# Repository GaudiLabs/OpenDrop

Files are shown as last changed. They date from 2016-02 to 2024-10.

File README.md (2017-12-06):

## OpenDrop 

Open Source Digital Microfluidics Bio Lab

### Don't click on the files!
Click on the "Download ZIP" Button to the right.
Then unpack the archive.

### Open Source Digital Microfluidics Bio Lab

OpenDrop is a new design for an open source digital microfludics platform for research purposes. The device uses recent electro-wetting technology to control small droplets of liquids. Potential applications are lab on a chip devices for automating processes of digital biology. How ever the present design should also open the technology to other field and allow experimentation to find new applications. Including the field of art, music, games and education.

For more info on the open source project see:

http://www.gaudi.ch/OpenDrop

### License

OpenDrop, all design files and software are licensed under a GNU GENERAL PUBLIC LICENSE
See license file in the repository.

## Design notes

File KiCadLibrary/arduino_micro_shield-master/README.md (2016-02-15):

arduino_micro_shield
====================

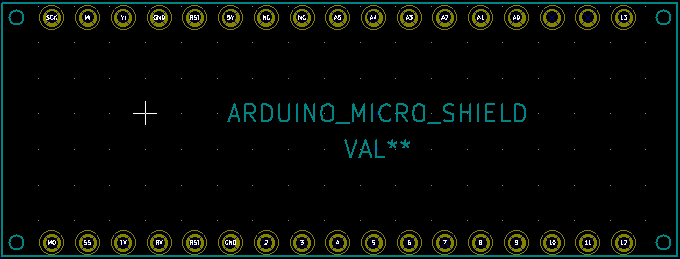
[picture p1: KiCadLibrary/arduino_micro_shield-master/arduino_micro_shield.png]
My image


KiCAD library and footprint for an Arduino Micro shield.

This is a component which represent the Arduino Micro pinout,
and a footprint for that component which maps to the surface area
and pinout of the Micro.

Pull requests very welcome!

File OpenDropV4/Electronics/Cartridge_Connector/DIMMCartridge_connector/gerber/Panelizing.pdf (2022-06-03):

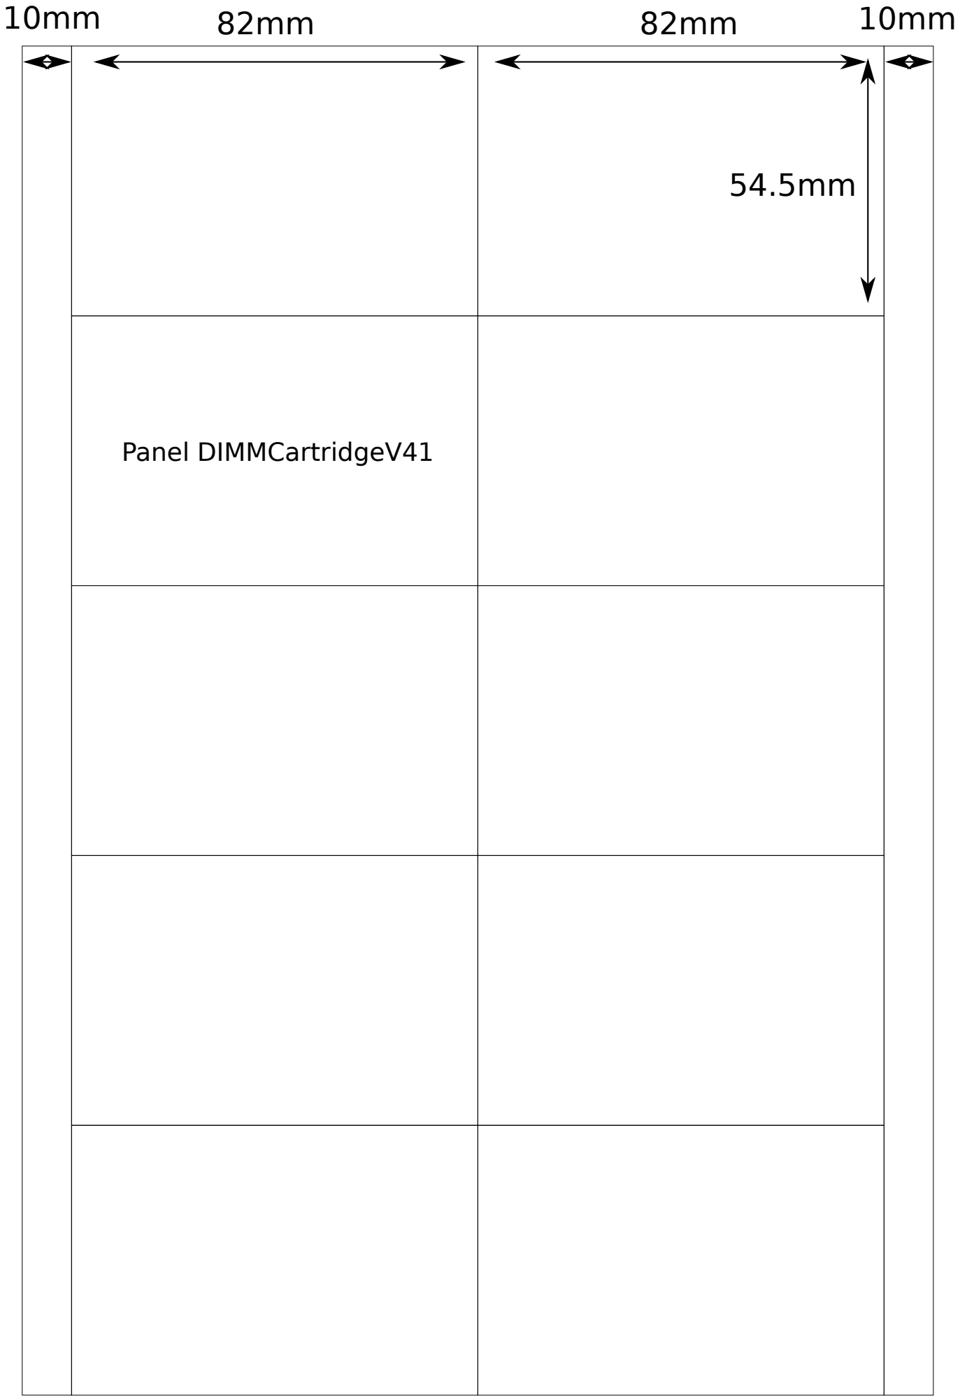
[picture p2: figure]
Panel DIMMCartridgeV41

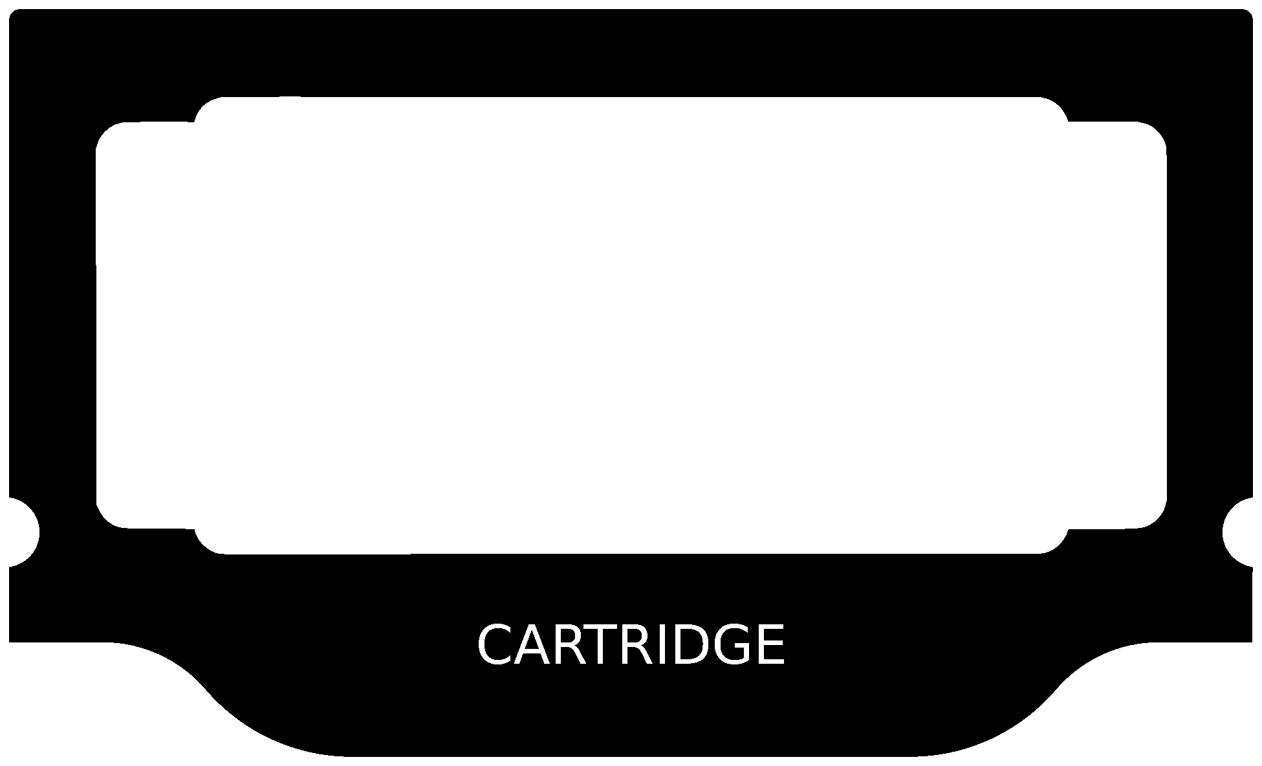
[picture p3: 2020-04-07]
OpenDropV4/Electronics/OpenFrame/design/DimmTopSilk.png

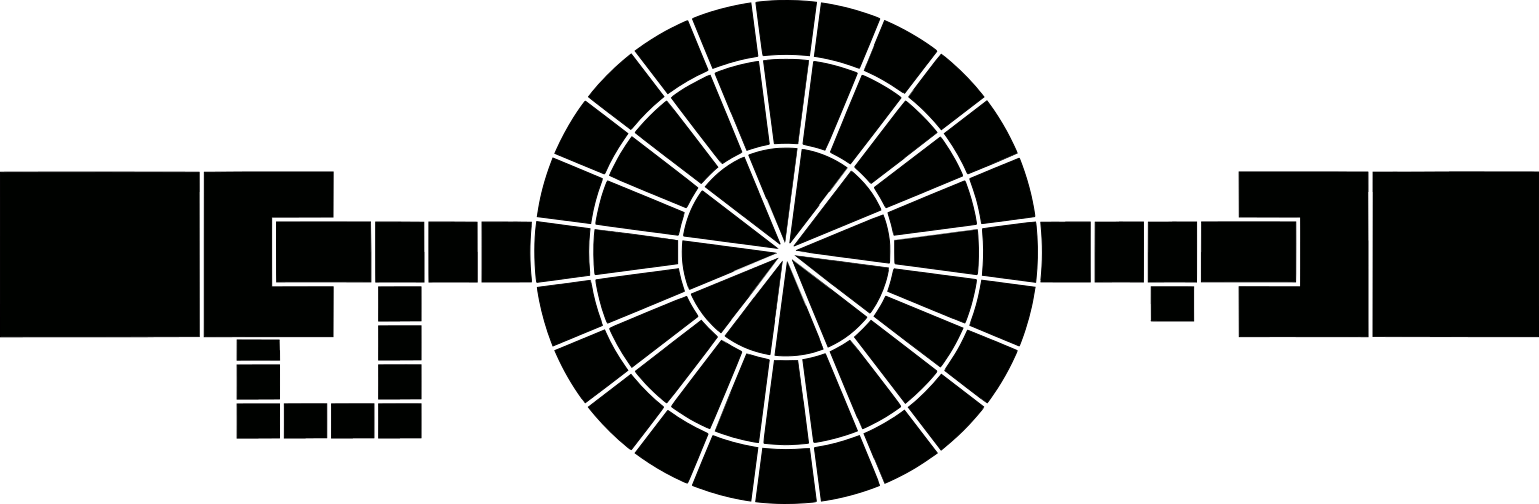
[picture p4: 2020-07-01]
OpenDropV4/Electronics/CartridgeV4/DIMMCartridgeV4/svg/path104085-4.png

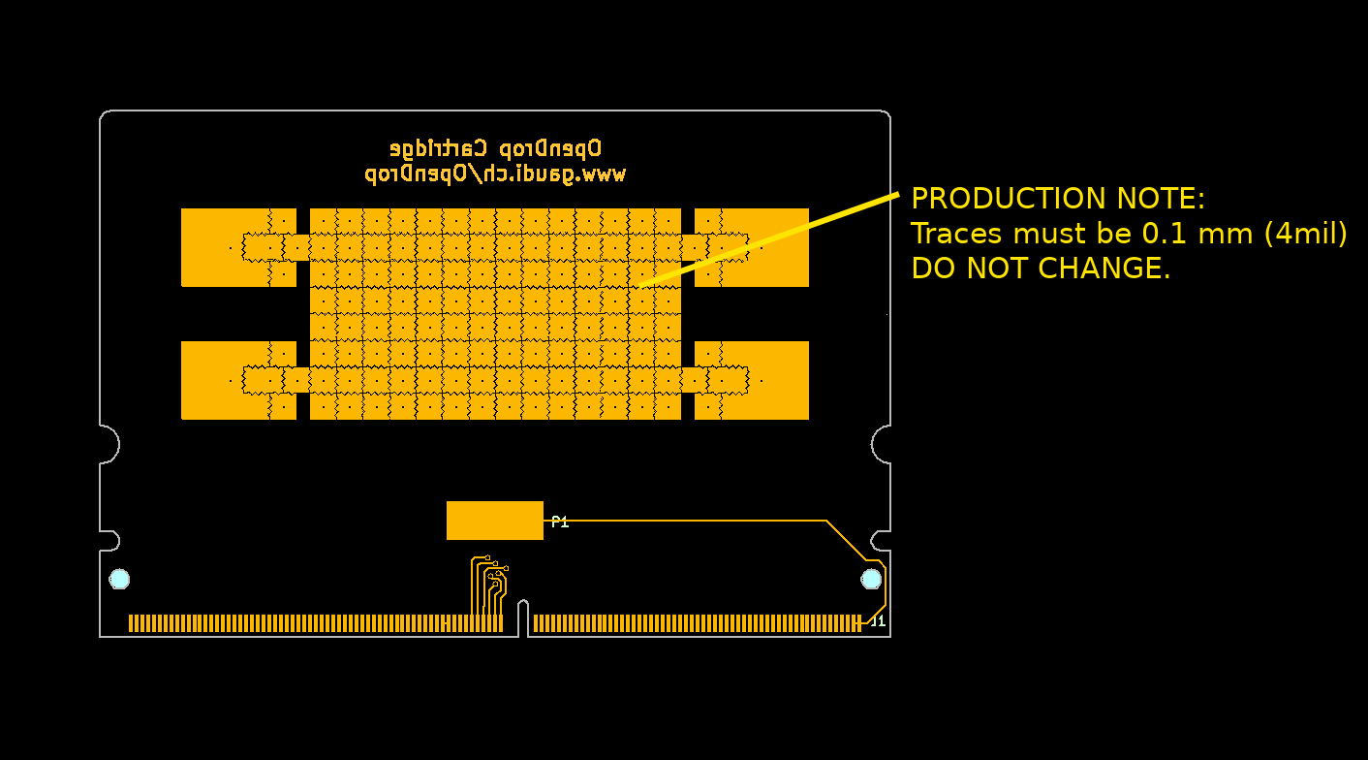
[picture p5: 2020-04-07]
OpenDropV4/Electronics/CartridgeV4/DIMMCartridgeV4/gerber/ProductionNote.png

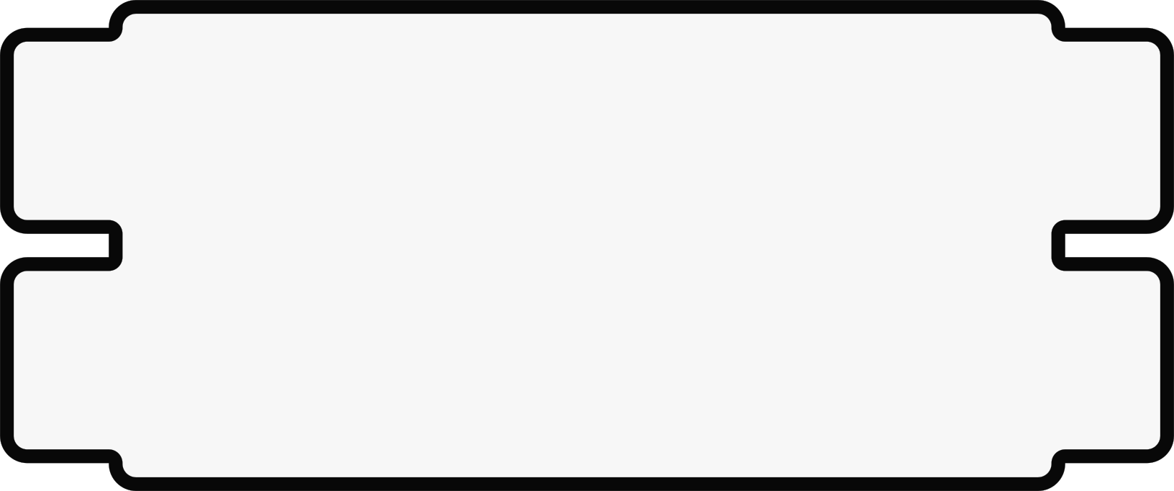
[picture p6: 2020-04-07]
OpenDropV4/Electronics/CartridgeV4/DIMMTop/design/DimmTopCooper.png

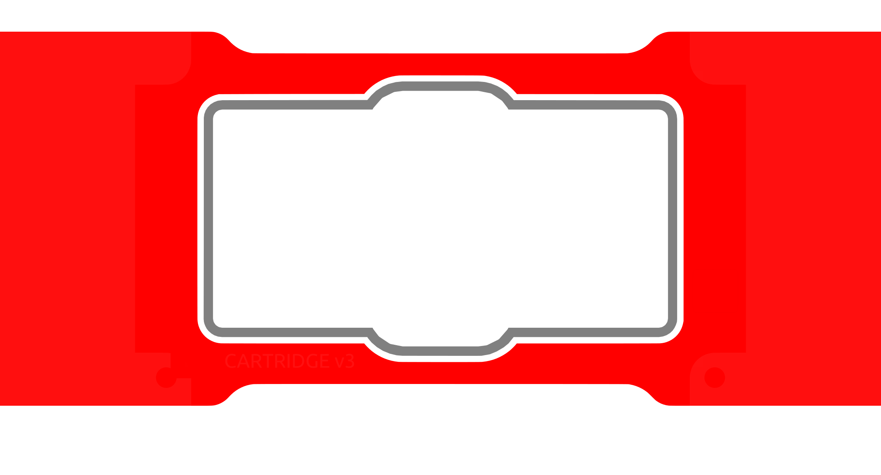
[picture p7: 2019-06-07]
OpenDropController4_25/OpenDropFrame.png

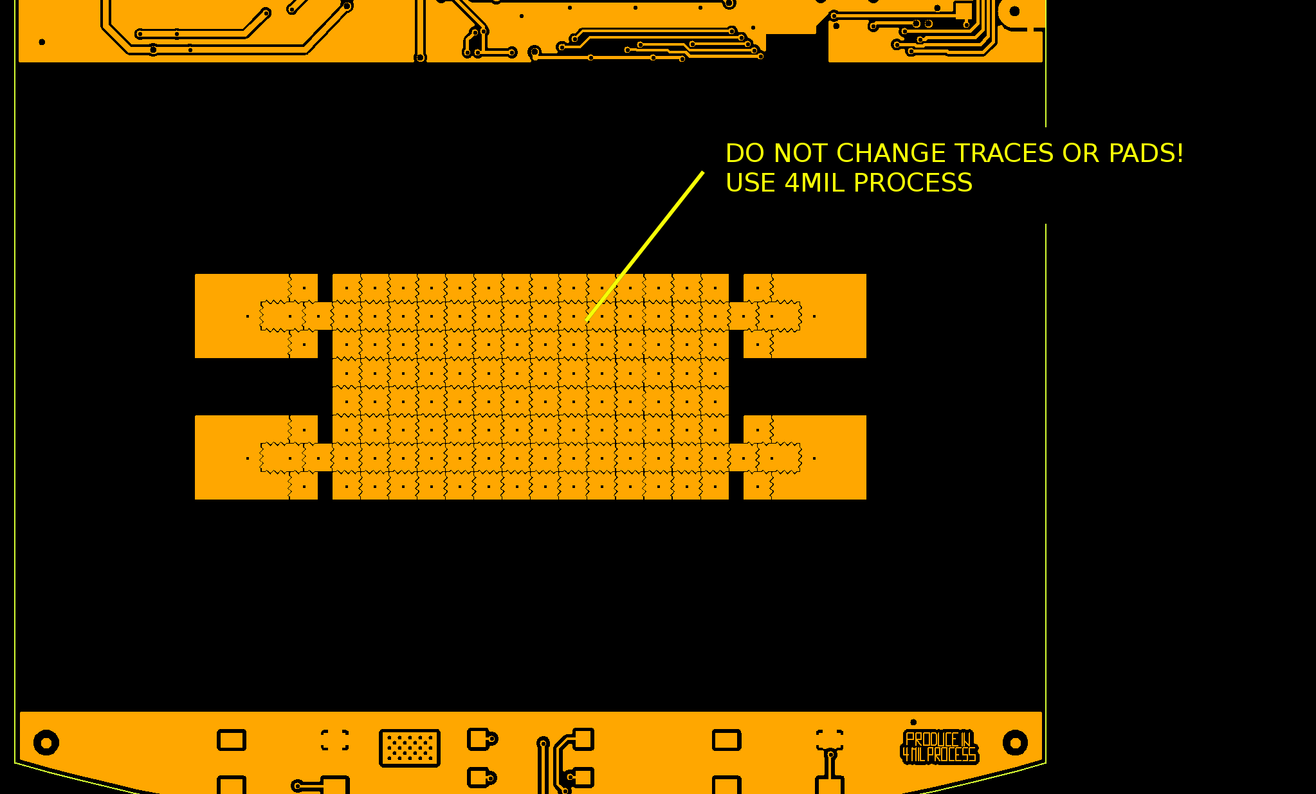
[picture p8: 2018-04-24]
OpenDropV4/PCB/OpenDropV4/Gerber/ProductionNote_OpenDropV3.png

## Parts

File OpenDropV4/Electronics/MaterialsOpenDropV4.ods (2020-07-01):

 | Materials OpenDrop V4 |  | 19. Mai 2020
 | Quantity | Designation | Order No | Manufacturer
Main Board
 | 1 | Switch_On-On | SS 25136 NH, 642-ADTSM62RVTR 642-25136NLDH | Reichelt Mouser
 | 4 | Spacer | DI 15MM | reichelt
 | 4 | Screws M3x 8mm | BN1435.03008 | Hasler.ch /bossard
 | 1 | Speaker16mm |  | aliexpress
 | 1 | OLED_096_1 |  | BuyDisplay / R2
 | 1 | Main Board |  | PCBGogo
 | 1 | 5mm Acrylic |  | FabLab
 | 1 | Polypropylenfolie PP / EVACAST 1070 N16 sand-mat 0.8 mm | Art. No 107807 | VINK
 | 1 | Joystic Cap |  | 3D Printed
 | 1 | Connector Cover |  | 3D Printed
 | 1 | Cartridge Bar |  | 3D Printed
 | 4 | Rubber Feets |  | ebay
Driver Board
 | 2 | HV507 Driver | 689-HV507PG-G HV507PG-G-ND | Microchip DigiKey
 | 1 | DIMM Connector 0.6MM DDR3 MINIDIMM SKT 244P RA SMT AU | 538-87918-0301 | mouser
 | 1 | FFC & FPC Connector 0.5 ZIF BTM CONT | 538-505278-2433 | mouser
 | 1 | FFC / FPC Jumper Cable 0.50 Type D 2 4 ckts lgt 30 | 538-15166-0250 | mouser
 | 1 | Driver Board PCB |  | PCBWay
Cartridge
 | 1 | DIMM_Frame |  | PCBWay
 | 1 | DIMM_Cartridge |  | PCBGogo
 | 1 | DIMM_Top |  | PCBWay
 | 1 | Double Sided Capton Tape |  | ebay
 | 1 | ITO Glass | 100x40x1.1 / 60x31 / 60.5x31.5 | ebay
 | 1 | Fluoropel Coating |  | Cytonix
 | 1 | ETFE Foil
 | 1 | Silicon Glue |  | mouser
 | 1 | Conductive Tape |  | mouser
 | 1 | Bag |  | reichelt
Open Cartridge | 1 | Open_Frame
 | 2 | Clips |  | 3D Printed
 | 1 | Parafilm
 | 1 | Silicon Oil
 | 1 | Bag
 | 1 | Grounding Wire Clip
 | 1 | Grounding Wire Pin
 | 1 | Shipping
 | 1 | Packaging
 | 1

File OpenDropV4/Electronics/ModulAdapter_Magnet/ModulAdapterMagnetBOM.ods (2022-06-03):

 | BOM Modul Adapter Magnet
 |  |  |  |  |  |  |  | 16 | 16
Id | Designator | Package | Quantity | Designation | Supplier and ref
5 | J1 | MiniDimm_06_244_200 | 1 | Mini_Dimm_244 | 87918-0301 | 538-87918-0301 |  | 16 | 16 | 32
9 | J2 | FFC_MOLEX_EASYON_05mm_24 | 1 | Conn_01x24_Female | 505278-2433 | 538-505278-2433 |  | 16 | 16 | 100
12 | U1 | P-VQFN16-0303-0.50-001 | 1 | TC78H660FTG | 757-TC78H660FTGEL |  |  | 16 |  | 32
3 | U3 | SSOP-20_5.3x7.2mm_P0.65mm | 1 | MCP23008_SS | 579-MCP23008-E/SS |  |  | 16 |  | 20
6 | U4,U2 | PQFP-80_14x20mm_Pitch0.8mm | 2 | HV507 | 689-HV507PG-G |  |  | 32 | 32 | 64
15 | C1,C4,C12,C13 | C_0603_1608Metric | 4 | 100nF | 603-CC603KRX7R8BB104 |  |  | 64 |  | 4000
13 | C2 | C_0805_2012Metric | 1 | 10uF | 81-GRM188R61A106ME9D |  |  | 16 |  | 200
16 | C3,C5 | C_0603_1608Metric | 2 | 22nF | 80-C0603C223K5R |  |  | 32 |  | 200
17 | R1 | R_0603_1608Metric | 1 | 100k | 603-RC0603FR-07100KL |  |  | 16 |  | 5000
18 | R2 | R_0603_1608Metric | 1 | 47k | 603-RC0603FR-0747KL |  |  | 16 |  | 1000
14 | R3,R7 | R_0603_1608Metric | 2 | 4.7k | 603-RC0603FR-074K7L |  |  | 32 |  | 1000
4 | R4,R5,R6,R8 | R_0603_1608Metric | 4 | 10k | 603-RC0603FR-0710KL |  |  | 64 |  | 2000
1 | M1 | GreaMotor6mm_Magnet | 1 | Motor_DC | 242 | 136 | 3 stage | 16
2 | M2 | GreaMotor6mm_Magnet_l | 1 | Motor_DC | Type Model NFP609-136-0675 |  |  | 16
 |  |  |  |  | Standard Shaft
 |  |  |  |  | FU HAORAN
 |  |  |  |  | https://nfpshop.com/shop
 |  | Magnet | 2 | S-03-02-N | Supermagnete.ch

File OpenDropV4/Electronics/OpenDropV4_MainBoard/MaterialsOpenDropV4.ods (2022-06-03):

 | Materials OpenDrop V4 |  | 19. Mai 2020
 | Quantity | Designation | Order No | Manufacturer | Price / pcs | Price
Main Board |  |  |  |  |  | Quantity | 30
 | 1 | Switch_On-On | SS 25136 NH, 642-ADTSM62RVTR 642-25136NLDH | Reichelt Mouser | 2.30 € | 2.30 € | 30
 | 4 | Spacer | DI 15MM | reichelt | 0.13 € | 0.52 € | 120 |  |  | 200
 | 4 | Screws M3x 8mm | BN1435.03008 | Hasler.ch /bossard | 0.04 € | 0.16 € | 120
 | 2 | Screws M3x 12mm | BN1435.03012 | Hasler.ch /bossard | 0.04 € | 0.08 € | 60
 | 1 | Speaker16mm |  | aliexpress | 0.50 € | 0.50 € | 30
 | 1 | OLED_096_1 |  | BuyDisplay / R2 | 3.00 € | 3.00 € | 30
 | 1 | Main Board |  | PCBGogo | 38.33 € | 38.33 € | 30
 | 1 | 5mm Acrylic |  | FabLab | 2.00 € | 2.00 € | 30
 | 1 | Polypropylenfolie PP / EVACAST 1070 N16 sand-mat 0.8 mm | Art. No 107807 | masterplatex.de VINK | 0.11 € | 0.11 € | 30
 | 1 | Joystic Cap |  | 3D Printed |  | 0.00 € | 30
 | 1 | Connector Cover |  | 3D Printed |  | 0.00 € | 30
 | 1 | Cartridge Bar |  | 3D Printed |  | 0.00 € | 30
 | 4 | Rubber Feets |  | ebay |  | 0.00 € | 120
 | 1 | USB Cable
Driver Board |  |  |  |  |  | Quantity | 30 |  |  |  | Preise CHF | 2021
 | 2 | HV507 Driver | 689-HV507PG-G HV507PG-G-ND | Microchip DigiKey | 11.85 € | 23.70 € | 60 | 12 |  | 711.00 € | 12.22 | 24.44
 | 1 | DIMM Connector 0.6MM DDR3 MINIDIMM SKT 244P RA SMT AU | 538-87918-0301 | mouser | 12.58 € | 12.58 € | 30 | 6 |  | 377.40 € | 14.55 | 14.55
 | 1 | FFC & FPC Connector 0.5 ZIF BTM CONT | 538-505278-2433 | mouser | 0.59 € | 0.59 € | 30 | 60 |  |  | 0.638 | 0.638
 | 1 | FFC / FPC Jumper Cable 0.50 Type D 2 4 ckts lgt 30 | 538-15166-0250 | mouser | 1.81 € | 1.81 € | 30
 | 1 | Driver Board PCB |  | PCBWay | 1.80 € | 1.80 € | 30 |  |  |  |  | 39.628 | chf
Cartridge |  |  |  |  |  | Quantity | 50 |  |  |  |  | 43.5 | usd
 | 1 | DIMM_Frame |  | PCBWay | 0.46 € | 0.46 € | 50 |  | 20 |  |  | 1305
 | 1 | DIMM_Cartridge |  | PCBGogo | 2.16 € | 2.16 € | 50 |  | 60
 | 1 | DIMM_Top |  | PCBWay | 0.49 € | 0.49 € | 50 |  | 30 |  | PCBgogo | 1450
 | 1 | Double Sided Capton Tape |  | ebay | 0.60 € | 0.60 € | 50
 | 1 | ITO Glass | 100x40x1.1 / 60x31 / 60.5x31.5 | ebay | 1.94 € | 1.94 € | 50 |  |  |  |  | 1.11111111111111
 | 1 | Fluoropel Coating |  | Cytonix | 1.00 € | 1.00 € | 50
 | 1 | ETFE Foil |  |  |  | 0.00 € | 50
 | 1 | Silicon Glue | DC 184, Dow Corning, Sylgard | Suter Kunststoffe AG Swiss-composite.ch | 278.70 € | 278.70 € | 50
 | 1 | Conductive Tape, 3M 1/2-5-9719 | 3M156174-ND | mouser | 34.50 € | 0.35 € | 50
 | 1 | Bag | ESD BEUTEL-S 127 | reichelt |  | 0.00 € | 50
 |  |  |  |  |  | Quantity | 30
Open Cartridge | 1 | Open_Frame |  |  | 0.76 € | 0.76 € | 30
 | 2 | Clips |  | 3D Printed |  |  | 60
 | 1 | Parafilm |  |  |  |  | 30
 | 1 | Silicon Oil |  |  |  |  | 30
 | 1 | Bag |  |  |  |  | 30
 | 1 | Grounding Wire Clip |  |  |  |  | 30
 | 1 | Grounding Wire Pin |  |  |  |  | 30
 | 1 | Shipping |  |  | 24.00 € | 24.00 €
 | 1 | Packaging |  |  | 5.00 € | 5.00 €
 | 1 |  |  |  |  | 0.00 €

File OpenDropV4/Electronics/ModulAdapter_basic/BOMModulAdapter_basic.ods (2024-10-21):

 | BOM OpenDrop Basic Adapter
Id | Designator | Package | Quantity | Designation
4 | J1 | MiniDimm_06_244_200 | 1 | Mini_Dimm_244
 |  |  |  | ATSAMD21G18A-MUT
7 | U4,U2 | PQFP-80_14x20mm_Pitch0.8mm | 2 | HV507
8 | J2 | FFC_MOLEX_EASYON_05mm_24 | 1 | Conn_01x24_Female
 | R1,R2, | R_0603_1608Metric | 2 | 4.7k (10k)
11 | C1,C4,C12,C13,C9,C10 | C_0603_1608Metric | 6 | 100nF
19 | J5 | Tag-Connect_TC2030-IDC-NL_2x03_P1.27mm_Vertical | 1 | Conn_02x03_Odd_Even
26 | H1,H2,H3,H4 | MountingHoleM3 | 4 | MountingHole
15 | J3,J4 | PinHeader_2x02_P2.00mm_Vertical | 2 | Conn_02x02_Top_Bottom
 |  | Magnet

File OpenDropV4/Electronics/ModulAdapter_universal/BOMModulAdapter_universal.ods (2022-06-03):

 | BOM OpenDrop Universal Adapter
Id | Designator | Package | Quantity | Designation | Supplier and ref
4 | J1 | MiniDimm_06_244_200 | 1 | Mini_Dimm_244 | 87918-0301 | 538-87918-0301
2 | U5 | QFN-48-1EP_7x7mm_P0.5mm_EP5.15x5.15mm | 1 | SAMD21G18B
7 | U4,U2 | PQFP-80_14x20mm_Pitch0.8mm | 2 | HV507 | 689-HV507PG-G
8 | J2 | FFC_MOLEX_EASYON_05mm_24 | 1 | Conn_01x24_Female | 505278-2433 | 538-505278-2433
9 | U1 | P-VQFN16-0303-0.50-001 | 1 | TC78H660FTG | 757-TC78H660FTGEL
23 | Q1,Q3,Q5 | SOT-23 | 3 | Q_NMOS_GSD | 863-NTR3C21NZT1G |  | AO3420
20 | Q2,Q4,Q6 | SOT-23 | 3 | PMOS |  |  | AO3403 | DMP3160L-7
21 | Y1 | Crystal_SMD_3215-2Pin_3.2x1.5mm | 1 | 32 765
 | R1,R2, | R_0603_1608Metric | 2 | 4.7k (10k) | 603-RC0603FR-074K7L
14 | R6 | R_0603_1608Metric | 1 | 4.7k (10k) | 603-RC0603FR-074K7L
10 | R3,R7 | R_0603_1608Metric | 2 | 4.7k | 603-RC0603FR-074K7L
 | R15,R16,R17 | R_0603_1608Metric | 3 | 4.7k 0.1% | RT0201BRD074K7L
12 | R4 | R_0603_1608Metric | 1 | 100k | 603-RC0603FR-07100KL
13 | R5 | R_0603_1608Metric | 1 | 47k | 603-RC0603FR-0747KL
16 | R9,R10,R11,R12, | R_0603_1608Metric | 9 | 10k | 603-RC0603FR-0710KL
11 | C1,C4,C12,C13,C9,C10 | C_0603_1608Metric | 6 | 100nF | 603-CC603KRX7R8BB104
17 | C6 | C_0603_1608Metric | 1 | 1uF
18 | C7,C8 | C_0603_1608Metric | 2 | 22pF
22 | C2 | C_0603_1608Metric | 1 | 10uF | 81-GRM188R61A106ME9D
24 | C3 | C_0603_1608Metric | 1 | 22nF | 80-C0603C223K5R
19 | J5 | Tag-Connect_TC2030-IDC-NL_2x03_P1.27mm_Vertical | 1 | Conn_02x03_Odd_Even
26 | H1,H2,H3,H4 | MountingHoleM3 | 4 | MountingHole
6 | M2 | GreaMotor6mm_Magnet | 1 | Motor_DC | 242 | 136 | 3 stage
3 | M1 | GreaMotor6mm_Magnet_l | 1 | Motor_DC | Type Model NFP609-136-0675
 |  |  |  |  | Standard Shaft
 |  |  |  |  | FU HAORAN
 |  |  |  |  | https://nfpshop.com/shop
15 | J3,J4 | PinHeader_2x02_P2.00mm_Vertical | 2 | Conn_02x02_Top_Bottom
 |  | Magnet

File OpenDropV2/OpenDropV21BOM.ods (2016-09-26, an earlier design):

 | BOM OpenDrop V2.1
 | Designator | Quantity | Designation | Package | Supplier and ref | Order No. | Order No. DigiKey | Price / pcs | Price |  | Stock | Order |  | New Order
 | U2,U4 | 2 | HV507 | PQFP-80_14x20mm_Pitch0.8mm | Digikey | HV507PG-G-ND | HV507PG-G-ND | 12.00 € | 24.00 € | d | 8 | 0 |  | d | 12x mouser
 | U6 | 1 | MCP6002 | SO08 | reichelt | MCP 6002-I/SN | MCP6002T-I/SNCT-ND | 0.33 € | 0.33 € | d |  | 4 |  | d | ok mouser
 | T1 | 1 | IRF 840S | D2PAK | reichelt.de | IRF 840S | IRF840SPBF-ND / IRF840ASTRLPBFCT-ND | 1.02 € | 1.02 € | r | 1 | 3 |  | 40 ??? | ok mouser
 | U1 | 1 | MAX1771ESA | SO08 | farnell | 2518765 | MAX1771ESA+CT-ND | 4.25 € | 4.25 € | f | 4 | 0 |  | 40 | 1379871
 | Q1,Q2,Q3,Q5,Q6,Q7 | 6 | BSS138 | SOT-23 | reichelt | BSS 138 SMD | BSS138CT-ND | 0.05 € | 0.30 € | r | 8 | 16 |  | 240
 | D1 | 1 | ES2F | DO-214AA | farnell | 2306320 | ES2F-E3/52TGICT-ND | 0.07 € | 0.07 € | f | 5 | -1 |  | 40
 | D2,D3,D4,D5 | 4 | 1N4148 | SOD-323 | reichelt | 1N 4148 WS | 1N4148WXTPMSCT-ND | 0.04 € | 0.16 € | r | 7 | 9 |  | 160
 | LED2,LED3,LED4,LED5 | 4 | LED | LED_SIDE | reichelt.de | LW Y8SG / LB Y8SG | P14136CT-ND | 0.35 € | 1.40 € | r |  | 16 |  | 160
 | LED1 | 1 | LED | LED-0805 | reichelt.de | SMD-LED 0805 GN | 475-1410-1-ND | 0.07 € | 0.07 € | r | 2 | 2 |  | 40
 | LED8 | 1 | LED | LED-0805 | reichelt.de | SMD-LED 0805 BL |  | 0.07 € | 0.07 € | r | 5 | -1 |  | 40
 | C1 | 1 | 100uF, 35V | R_2512_HandSoldering | farnell | 1462445 | 478-3919-1-ND (16V) | 1.30 € | 1.30 € | d | 1 | 3 |  | 40
 | C2,C3,C11,C12,C13,C14 | 6 | 100nF | C_0805 | stock |  |  | 0.08 € | 0.48 € |  |  | 24 |  | ok
 | C4 | 1 | 4u7, 250V | C_SMD_12mm | farnell | 2326355 | PCE3432CT-ND (10uF) | 1.40 € | 1.40 € | f |  | 4 |  | 40
 | C5 | 1 | 10uF, 25V | C_1210_HandSoldering | farnell | 9302948 | 478-9408-1-ND / 718-1912-1-ND | 0.71 € | 0.71 € | f |  | 4 | ? | x | not needed
 | C6 | 1 | 100nF, 250V | C100n_250V | farnell | 1198358 | 720-1063-1-ND | 1.50 € | 1.50 € | f |  | 4 |  | 40
 | C7,C9,C15,C16 | 4 | 1uF | C_0805 | reichelt | X7R-G0805 1,0/25 | 1276-1066-1-ND | 0.05 € | 0.20 € | r |  | 16 |  | 160
 | C8,C10 | 2 | 2.2uF | C_0805 | reichelt | X7R-G0805 2,2/25 | 1276-1162-1-ND | 0.10 € | 0.20 € | r |  | 8 |  | 80
 | C17 | 1 | 1pF | C_0805 | farnell | 1759179 |  | 0.08 € |  | f |  | 4 |  | 40
 | L1 | 1 | 100uH | Inductor_18.54x15.24 | farnell | 3877693 | 495-2703-1-ND | 1.80 € | 1.80 € | d | 3 | 1 |  | 40
 | R1 | 1 | 6.8k | R_0805 | reichelt | SMD-0805 6,80K |  | 0.08 € | 0.08 € |  |  | 4 |  | 40
 | R17,R16,R15,R7 | 4 | 10k | R_0805_HeatPad | stock |  |  | 0.08 € | 0.32 € |  |  | 16 |  | ok
 | R2 | 1 | 1M5 | R_2512 | farnell | 9236058 | PT1.5MXCT-ND | 0.44 € | 0.44 € | d (x50) | 10 | -6 |  | d | ok mouser
 | R3 | 1 | 390k | R_0805 | reichelt | SMD-0805 390K |  | 0.08 € | 0.08 € |  |  | 4 |  | 40
 | R4,R6 | 2 | 390 | R_0805 | stock |  |  | 0.08 € | 0.16 € |  | 3 | 5 |  | ok
 | R5 | 1 | 15 | R_0805 | reichelt | SMD-0805 15,0 |  | 0.08 € | 0.08 € |  |  | 4 |  | 40
 | R8,R9,R10,R11,R12,R13 R14,R18,R19,R20,R21,R22,R23 R24,R25,R26,R27,R28,R29,R30 | 20 | 10k | R_0805 | stock |  |  | 0.08 € | 1.60 € |  |  | 80 |  | ok
 | R31 | 1 | 220k | R_0805 | stock |  |  | 0.08 € | 0.08 € |  |  | 4 |  | ok | 100k
 | RSENSE1 | 1 | 0R050 | R_2010 | farnell | 1100050 | CRM2010-FZ-R050ELFCT-ND | 0.77 € | 0.77 € | d | 4 | 0 |  | d | ok mouser 0.1Ohm
 | JS1 | 1 | JoystickSMD | JoystickSMD_SKQUSeries | farnell | 1435776 |  | 3.55 € | 3.55 € | f |  | 4 |  | 40
 | SW1,SW2 | 2 | SW_PUSH | PUSH_BUTTON_SMD | reichelt | TASTER 9314 | CKN9085CT-ND | 0.20 € | 0.40 € | d | 12 | -4 |  | d | ok mouser
 | POT1 | 1 | 5k Ohm | Potentiometer_Trimmer-Suntan-TSR-3386P | reichelt | 76-10 5,0K | 3386P-502LF-ND / 3386P-502TLF-ND | 0.30 € | 0.30 € | r | 2 | 2 |  | 40
 | SP1 | 1 | SPEAKER | SMD_PA12_Piezzo | reichelt | SMD-P12A03 | 490-4683-1-ND | 1.25 € | 1.25 € | r |  | 4 |  | 40
 | SW5 | 1 | SPST | Switch_On-On | reichelt | SS 25136 NH | 679-1887-ND | 1.94 € | 1.94 € | r | 1 | 3 |  | 40
 | J1 | 1 | DC_JACK | DC_JACK_SMD | reichelt | LUM 1613-14 | CP-002AHPJCT-ND | 0.92 € | 0.92 € | r | 1 | 3 |  | 40
 | Y1,Y2 | 2 | Pinheaders 17 pin |  | farnell | 1256661 | S4508-ND | 2.00 € | 4.00 € | f | 2 | 6 |  | 80
 |  | 4 | Distanzhülsen |  | reichelt | DI 20MM |  | 0.14 € | 0.56 € | r |  | 16 |  | 160
 | S1 | 1 | OLED_Connetor |  | farnell | 1356579 | 609-5204-1-ND | 0.60 € |  | d | 1 | 3 |  | d | ok mouser
 | U3 | 1 | ARDUINO_MICRO | ARDUINO_MICRO_SMD | ebay |  |  | 8.91 € | 8.91 € |  | 4 | 0 |  | 8
 |  | 1 | OLED_DISPLAY | OLED_096_1 | BuyDisplay |  | ER-OLED0.96-1B | 5.00 € | 5.00 € |  |  | 4 |  | ok
 | U5 | 1 | ESP8266_SMD | ESP8266_SMD | ebay |  |  | 1.99 € | 1.99 € |  |  | 4 |  | ?
1 | PCB | 1 |  |  | PCBWay |  |  | 10.00 € | 10.00 € |  |  | 4 |  | 8
1 | Acrylic Base | 1 |  |  |  |  |  | 2.00 € | 2.00 € |  |  | 4 |  | ok
 |  |  |  |  |  |  |  |  |  |  |  |  |  | Teile für Rüdigers Adapter bestellen
 | Screws |  |  |  |  |  |  |  | 83.69 €
 | Production
 | Buchsenleisten 2,54 mm, 1X04 |  |  |  | reichelt | MPE 094-1-004 |  |  | 251.07 €
 |  |  |  |  | Urs Gaudenz, GaudiLabs
 |  |  |  |  |  |  |  |  | 31.79 €
 |  |  |  |  |  |  |  |  | 7.486631016
 |  |  |  |  |  |  |  |  | 5.6 | 224 | 240.00 €
 |  |  |  |  |  |  |  |  | 16.6 | 664
 |  |  |  |  |  |  |  |  | 11.23 | 449.2
 |  |  |  |  |  |  |  |  | Bestellt für
 |  |  |  |  |  |  |  |  | 542
 |  |  |  |  |  |  |  |  | 404.4
 |  |  |  |  |  |  |  |  | 76.2

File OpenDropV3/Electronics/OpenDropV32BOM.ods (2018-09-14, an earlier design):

 | BOM OpenDrop V3 |  |  |  |  |  |  |  |  |  |  |  |  |  | 80 |  |  |  |  |  | 15
 | Version 3.2, August 2018
 | Designator | Quantity | Designation | Package | Note | Mouser | Manufacturer | Mouser Link | Manufacturer | Mouser by Joel | Digikey | Reichelt & Co | Price / pcs | Price |  |  |  |  | Bestellt | Stock | Bedarf
x | U2,U4 | 2 | HV507 | PQFP-80_14x20mm_Pitch0.8mm |  | 689-HV507PG-G |  |  | Microchip | https://www.mouser.com/ProductDetail/Microchip-Technology/HV507PG-G | HV507PG-G-ND |  | 11.89 € | 23.78 € | 160 |  | x |  | 0 | 0 | -30
x | U6 | 1 | MCP6002 | SO08 |  | 579-MCP6002T-I/SN |  |  | Microchip | https://www.mouser.com/ProductDetail/Microchip-Technology/MCP6002T-I-SN |  | MCP 6002-I/SN reichelt | 0.33 € | 0.33 € | 80 |  | x |  | lager |  | -15 |  | V3
x | T1 | 1 | TK560P60Y | DPAK(-3) (D-Pak_TO252AA) |  | 757-TK560P60YRQ |  |  | Toshiba | https://www.mouser.com/ProductDetail/Toshiba/TK560P60YRQ |  |  | 0.81 € | 0.81 € | 80 | digi | x |  | 3 | 3 | -12 |  | 757-TK5P50DT6RSS-Q | DPAK / TO-252 |  | Besser: | Neu: 757-TK560P60YRQ |  | Oder: stärker 511-STD15N50M2AG
x | U1 | 1 | MAX1771ESA | SO08 |  | 700-MAX1771CSAT |  |  | Maxim | https://www.mouser.com/ProductDetail/Maxim-Integrated/MAX1771CSA%2bT |  | 1379870 farnell | 4.70 € | 4.70 € | 80 |  | x |  | 3 | 2 | -13 |  | 942-IRFR825TRPBF
x | U7,U8,U9 | 3 | HCPL0534 |  |  | 630-ACPL-024L-000E (push-pull) 512-HCPL0534 (alt) |  |  | On Semi | https://www.mouser.com/ProductDetail/ON-Semiconductor-Fairchild/HCPL0534R2?qs=sGAEpiMZZMtd3yBnp8bAgBkEHX3sY6VPevhGfgNmg28%3d |  |  | 1.70 € | 5.10 € | 240 | digi | x |  | 9 | 7 | -38
x | U10,U11,U12,U13 | 4 | AQY210EHA |  |  | 769-AQY210EHA |  |  | Panasonic | https://www.mouser.com/ProductDetail/Panasonic-Industrial-Devices/AQY210EHAX |  |  | 1.34 € | 5.36 € | 320 | digi | x |  | 8 | 5 | -55
x | U14 | 1 | TLV1117LV33DCYR | SOT-223-4 |  | 595-TLV1117LV33DCYR |  |  | Texas Instruments | https://www.mouser.com/ProductDetail/Texas-Instruments/TLV1117LV33DCYR |  |  | 0.53 € | 0.53 € | 80 |  | x |  | 2 | 3 | -12
x | U3 | 1 | PAM8301 | SOT-23-6 |  | 621-PAM8301AAF |  |  | Diodes Inc | https://www.mouser.com/ProductDetail/Diodes-Incorporated/PAM8301AAF |  |  | 0.42 € | 0.42 € | 80 |  | x |  | 3 | 2 | -13
x | U5 | 1 | SAMD21G18B-A | TQFP-48_7x7mm_Pitch0.5mm |  | 556-ATSAMD21G18A-AU(T) |  |  | Microchip | https://www.mouser.com/ProductDetail/Microchip-Technology-Atmel/ATSAMD21G18A-AUT |  |  | 3.30 € | 3.30 € | 80 |  | x |  | 5 | 4 | -11
x | U15 | 1 | MCP41010 | SO08 |  | 579-MCP41010T-I/SN |  |  | Microchip | https://www.mouser.com/ProductDetail/Microchip-Technology/MCP41010T-I-SN |  |  | 1.43 € | 1.43 € | 80 |  | x |  | 3 | 3 | -12
x | U16 | 1 | 74xx14 | SOIC-14_N |  | 595-SN74AC14DR (595-SN74ACT14DR) |  | https://www.mouser.ch/ProductDetail/595-SN74AC14DR | Texas Instruments | https://www.mouser.com/ProductDetail/Texas-Instruments/SN74ACT14DR | 296-1068-1-ND |  | 0.35 € | 0.35 € | 80 |  | x |  | 4 | 4 | -11 |  | AC higher current than HC AC / HC = CMOS Level ACT / HCT TTL Level
x | D1 | 1 | ES2F | DO-214AA |  | 821-ES2F |  |  | Taiwan Semi | https://www.mouser.com/ProductDetail/Taiwan-Semiconductor/ES2F | ES2FA R3GCT-ND | 2306320 farnell | 0.50 € | 0.50 € | 80 |  | x |  | 3 | 8 | -7
x | D2,D3 | 2 | 1N4148 | SOD-323 |  | 512-1N4148WS |  |  | On Semi | https://www.mouser.com/ProductDetail/ON-Semiconductor-Fairchild/1N4148WS |  | 1N 4148 WS farnell | 0.04 € | 0.08 € | 160 |  | x |  | 10 | 10 | -20
x | LED1 | 1 | LED | LED-0805 |  | 859-LTST-C190TBKT |  |  | Lite On | https://www.mouser.com/ProductDetail/Lite-On/LTST-C190TBKT | 603? | SMD-LED 0805 BL | 0.13 € | 0.13 € | 80 |  | x |  | 10 | 11 | -4
x | LED2 | 1 | LED | LED-0805 |  | 859-LTST-C190KGKT |  |  |  |  | 603? | SMD-LED 0805 GN | 0.13 € | 0.13 € | 80 |  | x |  | 10 | 5 | -10
x | LED3 | 1 | LED | LED-0805 |  | 859-LTST-C190KRKT |  |  | Lite On | https://www.mouser.com/ProductDetail/Lite-On/LTST-C190KRKT | 603? | SMD-LED 0805 RT | 0.13 € | 0.13 € | 80 |  | x |  | 10 | 8 | -7
x | C1, C32 | 2 | 100uF, 35V | R_2512_HandSoldering |  | 581-TPSD107K016R0125 |  |  | AVX | https://www.mouser.com/ProductDetail/AVX/TPSD107K016R0125?qs=sGAEpiMZZMuEN2agSAc2pqveSFvydLQ7ik6YjlyIzQo%3d |  | 1462445, farnell | 1.30 € | 2.60 € | 160 |  | x |  | 4 | 5 | -25
x | C2,C3,C12,C13,C14,C22,C26,C30,C33,C34,C36 | 11 | 100nF | C_0805 | stock | 603-CC805KRX7R8BB104 |  |  | Yageo | https://www.mouser.com/ProductDetail/Yageo/CC0805KRX7R8BB104 |  |  | 0.08 € | 0.88 € | 880 | 1000 mouser? | x |  | lager |  | -165 |  | V3
x | C4, C18 | 2 | 3u9, 400V 4u7, 400V | C_SMD_12mm | farnell | 647-ULR2W3R9MNL1GS 647-ULR2G4R7MNL1GS 647-ULH2G7R5MNL1GS |  | https://www.mouser.ch/ProductDetail/647-ULH2G7R5MNL1GS | Nichicon | https://www.mouser.com/ProductDetail/Nichicon/ULR2G4R7MNL1GS | 2326355 |  | 0.90 € | 1.80 € | 160 |  | x |  | 6 | 6 | -24 |  | 647-ULR2W3R9MNL1GS 647-ULT2W3R3MNL1GS | 647-UUX2G4R7MNL1GS
x | C5, C21 | 2 | 22uF, 16V | C_1210_HandSoldering | farnell | TPSB226K016R0600 |  |  | AVX | https://www.mouser.com/ProductDetail/AVX/TPSB226K016R0600 | 9302948 |  | 0.65 € | 1.30 € | 160 |  | x |  | 10 | 8 | -22 | ?
x | C6, C35(opt) | 2 | 100nF neu? 10nF, 400V | 100nF 630V, 1913 |  | 80-C1808V104KBR /720-1063-1-ND / 667-ECW-U4103V17 |  |  | TDK | https://www.mouser.com/ProductDetail/TDK/C3216X7T2V104M160AA |  |  | 1.50 € | 3.00 € | 160 |  | x |  | 5 | 4 | -26 |  | DigiKey PCF1412CT-ND |  | 80-LDEME3100KA5N00
x | C7,C9,C11,C15,C16,C20,C24,C27 | 8 | 1uF | C_0805 | reichelt | 810-C2012X7R1C105M-3 603-CC805KKX7R7BB105 |  |  | Yageo | https://www.mouser.com/ProductDetail/Yageo/CC0805KKX7R7BB105 |  | X7R-G0805 1,0/25, reichelt | 0.05 € | 0.40 € | 640 |  | x |  | 30 | 21 | -99
x | C8,C10 | 2 | 2.2uF | C_0805 | reichelt | 603-CC805KKX7R7BB225 |  |  | Yageo | https://www.mouser.com/ProductDetail/Yageo/CC0805KKX7R7BB225 |  | X7R-G0805 2,2/25, reichelt | 0.10 € | 0.20 € | 160 |  | x |  | 10 | 10 | -20
x | C17 | 1 | 1pF | C_0805 | reichelt |  |  |  |  |  | NPO-G0805 1,0P |  | 0.08 € | 0.08 € | 80 |  | x |  | 0 |  | -15
x | C19 | 1 | 33uF, 35V 22uF 35VDC |  |  | 667-EEE-FK1V330P |  |  |  |  | use same as C5? |  | 0.20 € | 0.20 € | 80 |  | x |  |  | 2 | -13
x | C23,C25 | 2 | 22pF | C_0805 |  |  |  |  |  |  |  |  |  |  | 160 |  | x |  |  |  | -30
x | C28,C29 | 2 | 3.3nF ? | C_0805 |  |  |  |  |  |  |  |  |  |  | 160 |  | x |  |  |  | -30
x | C31 | 1 | 100nF (new) | C_0805 |  |  |  |  |  |  |  |  |  |  | 80 |  | x |  |  |  | -15
x | C37 | 1 | 470pF (new) | C_0805 |  |  |  |  |  |  |  |  |  |  | 80 |  | x
x | L1 | 1 | 100uH | Inductor_10x9.8 | mouser | SRN1060-101M |  |  |  |  | SRN1060-101MTR-ND |  | 0.48 € | 0.48 € | 80 |  | x |  | 4 | 3 | -12 |  |  | V3 | 150uH 1A 20 % 12.95x9.4mm SMD 871-B82476A1154M |  |  | B82464G4683M
x | R1 | 1 | 6.8k | R_0805 | stock |  |  |  |  |  |  |  | 0.08 € | 0.08 € | 80 |  | x |  |  |  | -15
x | R2 | 1 | 1M5 | R_2512 |  | 667-ERJ-1TYJ155U |  |  |  |  |  | 9236058, farnell | 0.44 € | 0.44 € | 80 |  | x |  | 4 | 2 | -13
x | R3,R9 | 2 | 390k | R_0805 | stock |  |  |  |  |  |  |  | 0.08 € | 0.16 € | 160 |  | x |  |  |  | -30
x | R11 | 1 | 15k (new) | R_0805 | stock |  |  |  |  |  |  |  | 0.08 € | 0.08 € | 80 |  | x |  |  |  | -15
x | R4,R6,R8,R13 | 4 | 390 | R_0805 | stock |  |  |  |  |  |  |  | 0.08 € | 0.32 € | 320 |  | x |  |  |  | -60
x | R5,R10,R18,R19,R20,R21,R22,R30,R44 | 9 | 10k | R_0805 | stock |  |  |  |  |  |  |  | 0.08 € | 0.72 € | 720 |  | x |  |  |  | -135
x | R31 | 1 | 15k | R_0805 | stock |  |  |  |  |  |  |  | 0.08 € | 0.08 € | 80 |  | x |  |  |  | -15
x | RSENSE1 | 1 | 0R10 | R_2010 |  | 652-CRL2010JWR100ELF |  |  |  |  |  | 1100050, farnell | 0.77 € | 0.77 € | 80 |  | x |  | 3 | 3 | -12
x | R39 | 0 | 5.6k (6.8k?) (new) (not needed with push pull) |  |  |  |  |  |  |  |  |  |  |  | 0
x | R12,R33,R35,R38,R42,R43 | 1 | 2.2k (not needed with push pull) | R_0805 | stock |  |  |  |  |  |  |  | 0.08 € | 0.08 € | 80 |  | x |  |  |  | -15
x | R32,R34,R36,R40,R41,R45,R48,R49,R51 | 9 | 220R | R_0805 | stock |  |  |  |  |  |  |  | 0.08 € | 0.72 € | 720 |  | x |  |  |  | -135
x | R37 (new) | 1 | 220R (or 100R) |  |  |  |  |  |  |  |  |  |  |  | 80 |  | x
x | R7,R15,R16,R17 | 4 | 10R | R_0805_HeatPad | stock |  |  |  |  |  |  |  | 0.08 € | 0.32 € | 320 |  |  |  |  |  | -60
x | R29 (opt) | 1 | 680k | R_0805 |  |  |  |  |  |  |  |  |  |  | 80
x | R46, R47 | 2 | 5k (5.6k / 6,8k?) | R_0805 |  |  |  |  |  |  |  |  |  |  | 160 |  | x
x | R14,R23,R24,R25,R26,R27,R28 | 7 | 0R (new) | R_0805 |  |  |  |  |  |  |  |  |  |  | 560 |  | x
x | JS1 | 1 | JoystickSMD | SKQUDBE010, | JS5208 Series Datasheet | ALPS SKQUSeries |  |  |  |  | EG4561-ND ? | 1435776 farnell | 3.55 € | 3.55 € | 30 | 30 stock | x |  |  | 45 | 30
x | JS2 (option) | 1 | JoystickSMD (new) |  |  | SKRHABE010 |  |  |  |  |  |  |  |  | 50 |  | x
x | SW1,SW2 | 2 | SW_PUSH | PUSH_BUTTON_SMD | reichelt | 506-1571527-2 |  |  |  |  | black instead of brown? | TASTER 9314, reichelt | 0.32 € | 0.64 € | 160 |  | x |  | 9 | 5 | -25
x | SW3 | 1 | SW_PUSH | PUSH_BUTTON_SMD Right Angle | mouser | 611-KMS231GLFS |  |  |  |  |  |  | 0.54 € | 0.54 € | 80 |  | x |  |  | 0 | -15
x | SW5 | 1 | SPST | Switch_On-On | reichelt | 642-ADTSM62RVTR 642-25136NLDH |  |  |  |  |  | SS 25136 NH, reichelt | 1.94 € | 1.94 € | 80 | 35 |  |  | 2 | 9 | -6
x | J1 | 1 | USB-C | USB-C SMD Connector |  | 523-12401610E4#2A |  |  |  |  |  |  | 1.70 € | 1.70 € | 80 |  | x |  |  | 0 | -15
x | J2 | 1 | ISP PinHeaders 1.27 | Pin_Header_Straight_2x05_Pitch1.27mm_SMD |  | 649-202112100010C4LF |  |  |  |  |  |  | 0.56 € | 0.56 € | 80 |  | x |  | 5 | 4 | -11
x | S1 | 1 | OLED_Connetor |  | mouser | 649-SFV30R-1STE1HLF (bottom) – correct 649-SFV30R-2STE9HLF (top) |  |  |  |  |  |  | 0.72 € | 0.72 € | 80 |  | x |  | 5 | 5 | -10 |  | 649-SFV30R-1STE9HLF 649-SFV30R-2STE9HLF
x | Y1 | 1 | Crystal 32kHz | Crystal_SMD_3215-2pin_3.2x1.5mm |  | 449-LFXTAL009678REEL |  |  |  |  |  |  | 0.22 € | 0.22 € | 80 |  | x |  |  | 6 | -9
 |  | 4 | Spacers |  |  |  |  |  |  |  |  | DI 18MM, reichelt | 0.14 € | 0.56 € | 320 |  |  |  |  | 24 | -36
 |  | 4 | Screws | M3x 8mm |  |  |  |  |  |  |  |  |  |  | 320
x | SP1 | 1 | SPEAKER | Speaker16mm | aliexpress |  |  |  |  |  |  |  | 1.25 € | 1.25 € | 80 |  |  |  |  | 10 | -5
x | OLED | 1 | OLED_DISPLAY | OLED_096_1 | BuyDisplay / R2 |  |  |  |  |  |  |  | 5.00 € | 5.00 € | 80 |  |  |  |  | 12 | -3
x | PCB | 1 |  |  | PCBWay |  |  |  |  |  |  |  | 5.52 € | 5.52 € | 80 |  |  |  |  | 15 | 0
x | Acrylic Base | 1 |  | 5mm Acrylic |  |  |  |  |  |  |  |  | 2.00 € | 2.00 € | 80 |  |  |  |  | 1 | -14
x | Joystick Caps | 1 |  | Tact Tactile Push Button Switch Cap Silicone Clear/Black for 6x6mm Round Switch | ebay |  |  |  |  |  |  |  |  |  | 80 |  |  |  |  | 10
x | Assembling | 1 |  |  | R2 |  |  |  |  |  |  |  | 2.00 € | 2.00 € | 80 |  |  |  |  |  | -15
 | Packaging | 1 |  |  |  |  |  |  |  |  |  |  | 5.00 € | 5.00 € | 80 |  |  |  |  |  | -15
x | Registered Shipping | 1 |  |  |  |  |  |  |  |  |  |  |  |  | 80
x | REF | 2 | Fiducial_1mm_Dia_2.54mm_Outer_CopperTop
 |  |  |  |  |  |  |  |  |  |  |  |  | Bei 10 | 92.97 €
x | P14 | 1 | "MountingHolePad_3x9mm"
x | P16 | 1 | "MountingHolePad_3x9mm" |  |  |  |  |  |  |  |  |  |  |  | Electronic 63 chf | 63 |  | chf
x | P15 | 1 | "MountingHolePad_3x9mm" |  |  |  |  |  |  |  |  |  |  | 0.7297297297 | disp etc | 8.75 |  | chf
x | P13 | 1 | "MountingHolePad_3x9mm" |  |  |  |  |  |  |  |  |  | Bei 100 ca | 67.84 € |  | 15
x | P4 | 1 | "Measurement_Point_Square-SMD-Pad_Small" | "CONN_PSEUDO_AC"
x | P2 | 1 | "Measurement_Point_Croki" | "ScrewPad4"
x | P1,P3,P7,P8,P9,P10,P11,P12 | 8 | "Measurement_Point_Square-SMD-Pad_Small" |  |  |  |  |  |  |  |  |  | 75 | 5,625.00 €
 | Urs Gaudenz, GaudiLabs
 | Orders |  |  |  |  |  |  |  |  |  |  |  | 690.00 € | 825.00 CHF |  |  |  |  | 1.1956521739
 | 6. July 2017 |  | Phtot + DVD
 | 9. January 2017 |  | Theremin + |  |  |  |  |  |  |  |  |  | 490.00 € | 588.00 CHF |  |  |  |  | 1.2
 | 14. October 2016 |  | Theremin
 | 2. September 2016 |  | HV Chips |  |  |  |  |  |  |  |  |  | 575.00 € | 690.00 CHF |  |  |  |  | 1.2
 | 1. September 2016 |  | HV Chip + GnUSB
 | 16. August 2016 |  | LED usb Concet |  |  |  |  |  |  |  |  |  | 795.00 € | 954.00 CHF |  |  |  |  | 1.2
 | 10. August 2016 |  | MixTape
 | 20. June 2016 |  | OpenDrop ThereCoils, SpeakerSGMK Tape
 | 26. April 2016 |  | OpenDrop Digikey

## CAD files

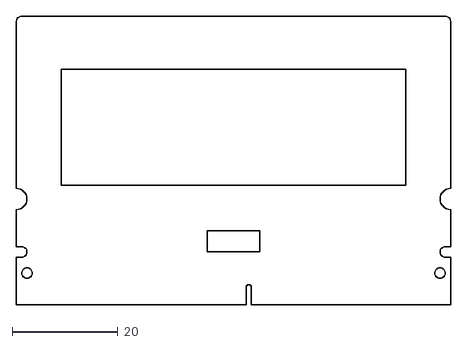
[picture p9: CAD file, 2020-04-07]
OpenDropV4/Electronics/CartridgeV4/DIMMCartridgeV4/Module_electrodes.dxf
82.0 x 54.5

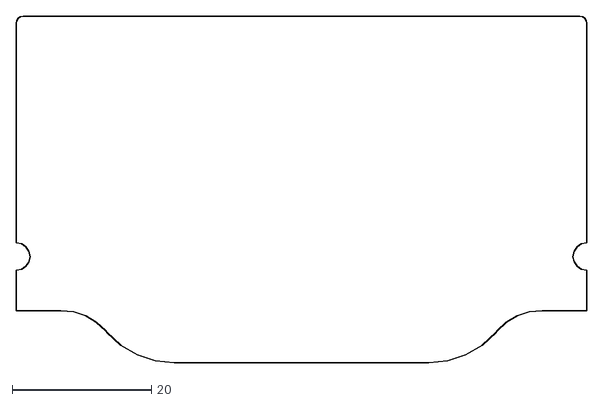
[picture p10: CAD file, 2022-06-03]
OpenDropV4/Electronics/CartridgeV4/DIMMCartridgeV4/svg/DimmMask.dxf
82.0 x 49.8

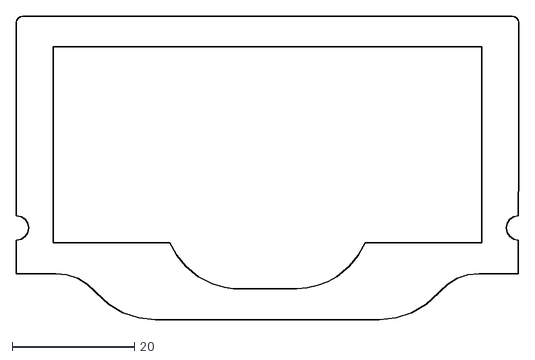
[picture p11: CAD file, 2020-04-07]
OpenDropV4/Electronics/CartridgeV4/DIMMFrame/DimmFrame.dxf
82.0 x 49.5

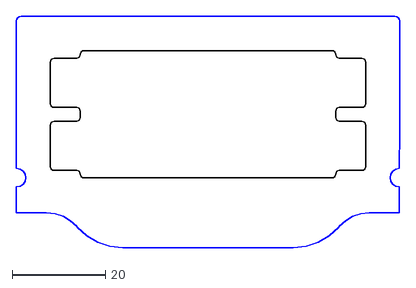
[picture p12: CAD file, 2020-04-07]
OpenDropV4/Electronics/CartridgeV4/DIMMTop/DimmTopOutline.dxf
82.0 x 49.5

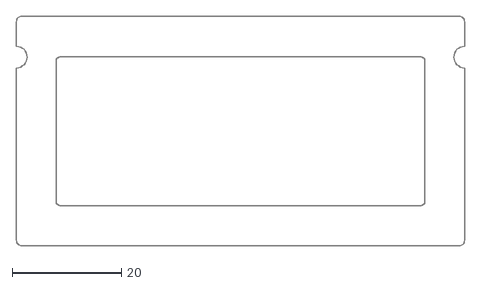
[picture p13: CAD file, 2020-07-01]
OpenDropV4/Electronics/OpenFrame/OpenFrame.dxf
82.0 x 42.0

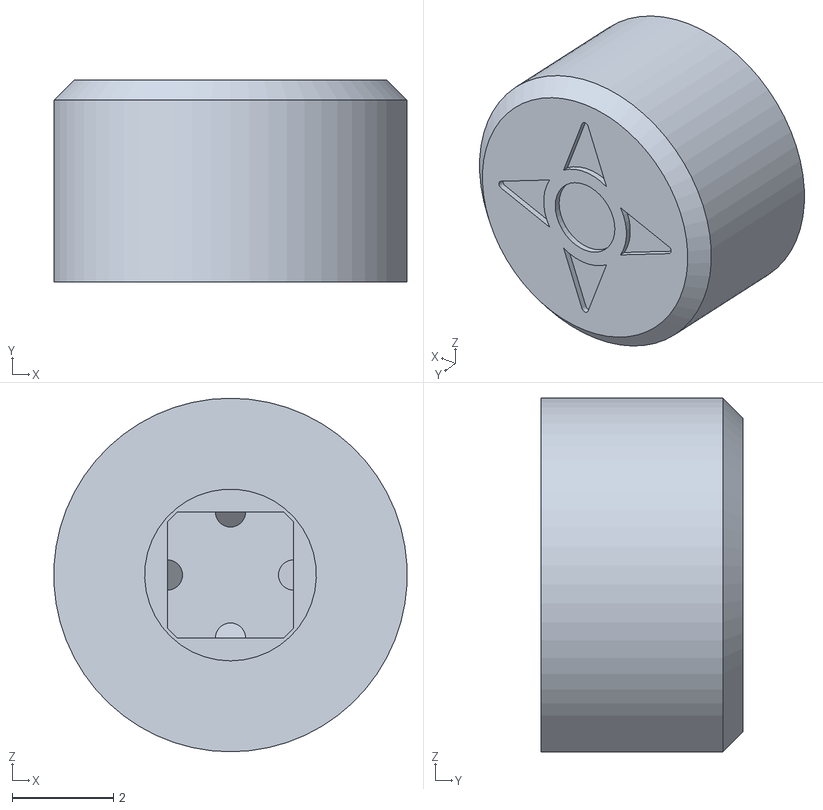
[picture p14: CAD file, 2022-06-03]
OpenDropV4/Hardware/OpenDropJoystickCapV4_cross.STL
6.99 x 4.00 x 7.00

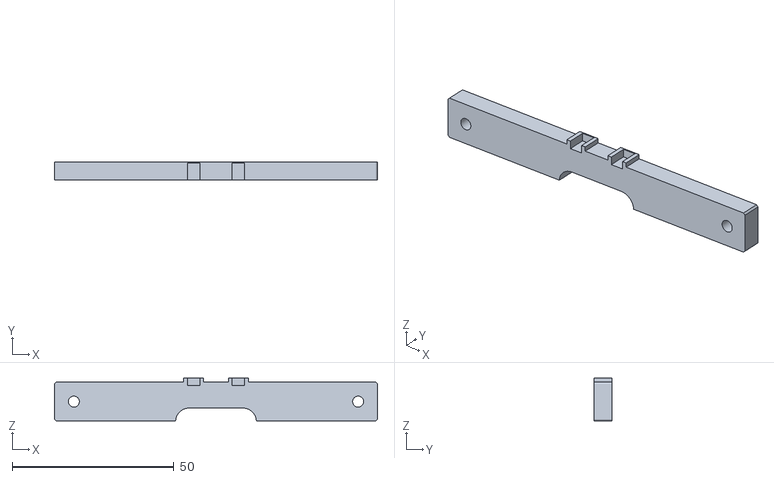
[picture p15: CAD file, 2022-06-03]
OpenDropV4/Hardware/CartridgBarMagnetV2.STL
100.0 x 5.60 x 13.3

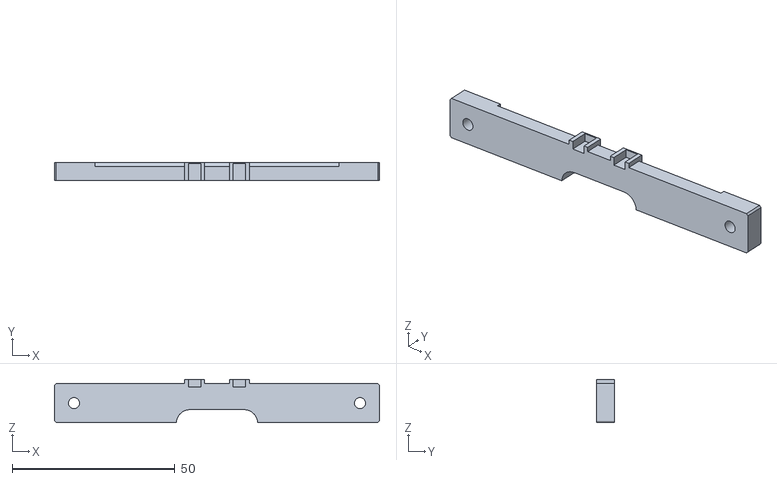
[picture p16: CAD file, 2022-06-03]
OpenDropV4/Hardware/CartridgBarUniversal.STL
100.0 x 5.60 x 13.3

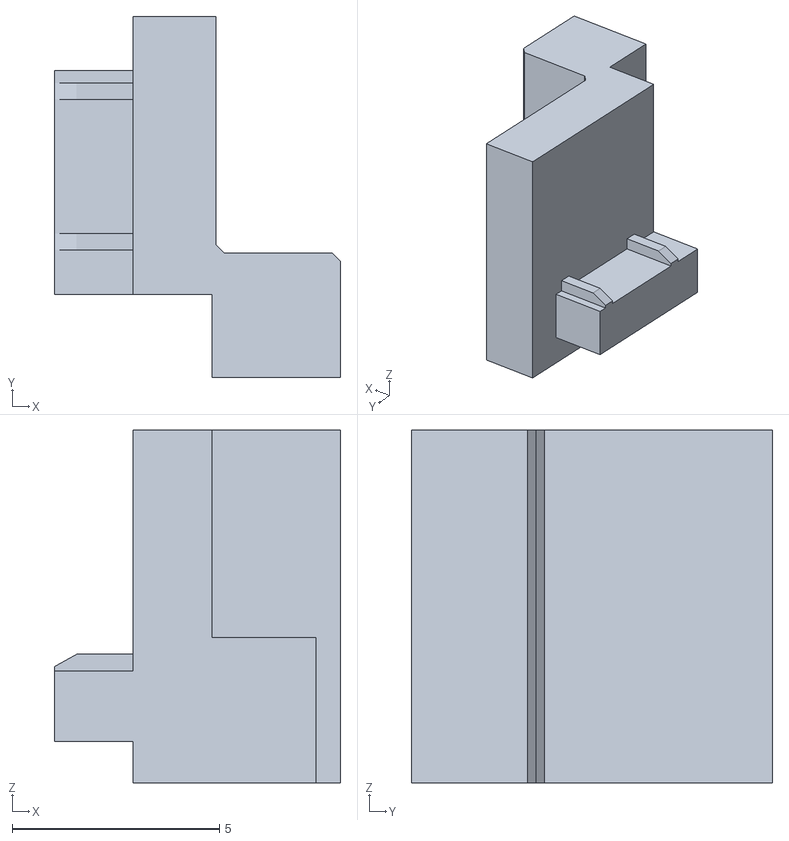
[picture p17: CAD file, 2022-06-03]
OpenDropV4/Hardware/TinyCover3.STL
6.90 x 8.70 x 8.50

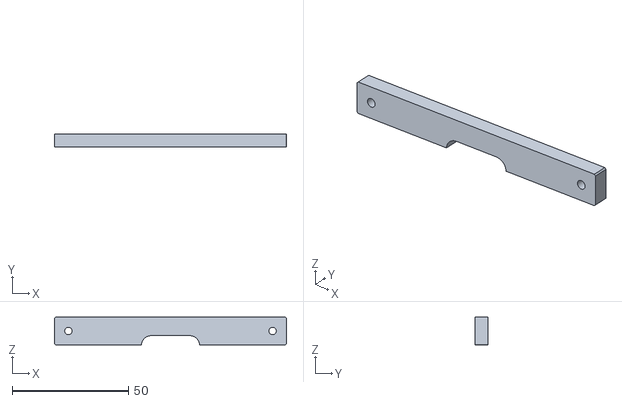
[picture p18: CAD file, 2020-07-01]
OpenDropV4/Hardware/CartridgBar.STL
100.0 x 5.60 x 12.0

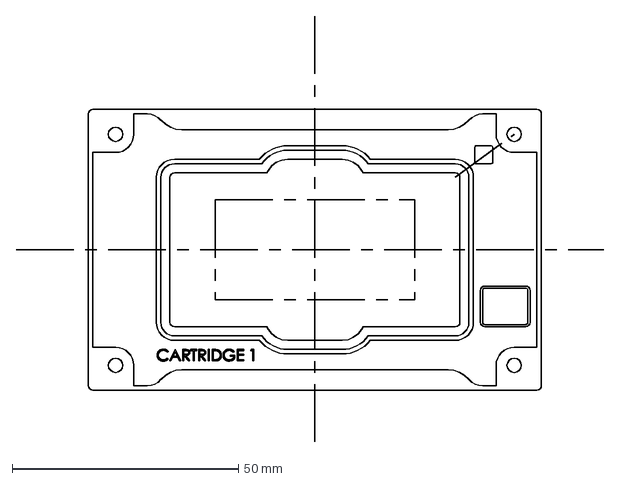
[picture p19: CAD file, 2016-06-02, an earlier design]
OpenDropV3/Carrier/PCBFrame/Cardridge_PCB.dxf
129.7 x 94.0 mm

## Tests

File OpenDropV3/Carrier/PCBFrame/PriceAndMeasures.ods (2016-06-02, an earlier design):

4mil | 66
hasl | 33
gold | 59 | 26 |  | 23
2 layer |  | 3 |  | 6
white |  | 5
black |  | 12
alu | 7
 |  |  |  |  | 55 | 78 | 23
10 | 13
20 | 25
50 | 39
 |  |  | 2.7
 |  |  |  | 100
 |  |  |  | 100 |  |  |  | y | 69
 |  |  | 56 | 57.65 | 144 | 145.65 |  | y | 131
 |  |  | 74.5 |  | 74.5
 |  |  |  |  |  |  |  | x | 149.5
 |  |  |  |  |  |  |  | x | 50.5
 |  |  | 144 | 145.65 | 56 | 57.65
 |  |  | 125.5 |  | 125.5
 |  |  |  |  |  |  |  | y | 83
 |  |  |  |  |  |  |  | y | 117
 |  |  |  |  |  |  |  | x | 130
 |  |  |  |  |  |  |  | x | 70
 |  |  | 34
 |  |  | 62
 |  |  | 28
 |  |  | 83

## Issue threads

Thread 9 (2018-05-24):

### ISSUE TITLE
Tantalum Cap Not Rated

### ISSUE THREAD

**Issue by biomurph** [GaudiLabs/OpenDrop#9]
The cap you specify in your BOM for C1 is not rated at 35V

https://www.mouser.com/ProductDetail/AVX/TPSD107K016R0125?qs=sGAEpiMZZMuEN2agSAc2pqveSFvydLQ7ik6YjlyIzQo%3d

It's rated at 16V. Do you have the correct part number for the 35V rating?

btw, I have boards from your design on order from PCB pool. Should arrive early next week.

**Comment by GaudiLabs** [comment]
Ok, cool. The version 3 has still bugs/things to improve. As I said I am just now working on fixing this and will push then. Please correct bugs or update when you see necessity. 

Urs


On 24 May 2018 18:06:01 CEST, Joel Murphy <notifications@github.com> wrote:
>Hey Urs,
>
>Yeah, I'm working on the badge.
>Thought I would go for your latest design with the ARM, and also
>thought it would be nice to have more people working on it with you.
>Yes, PCB Pool is Germany, I think. They also have offices in Ireland
>somehow...
>
>I did get feedback from their cam operator. Check the PDF (needs to be
>opened in acrobat to change layer visibility.
>
>Purchasing BOM now... What's the speaker you're using? Seems the BOM
>you have is out of date, as it specifies a micro USB connector. I found
>the Amphenol part on digikey.
>[02913i_w.pdf](https://github.com/GaudiLabs/OpenDrop/files/2036189/02913i_w.pdf)
>
>
>-- 
>You are receiving this because you commented.
>Reply to this email directly or view it on GitHub:
>https://github.com/GaudiLabs/OpenDrop/issues/9#issuecomment-391770301

-- 
Sent from my Android device with K-9 Mail. Please excuse my brevity.

**Comment by biomurph** [comment]
Will do. I think I will need to fork it again... had a github glitch on my end.

Cheers!

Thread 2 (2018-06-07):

### ISSUE TITLE
Do you have Bill of Materials of OpenDrop V2?

### ISSUE THREAD

**Issue by dr-data** [GaudiLabs/OpenDrop#2]

**Comment by GaudiLabs** [comment]
For the V21 the BOM is in the corresponding folder of the repo.

On July 6, 2016 9:33:57 AM GMT+02:00, dr-data <notifications@github.com> wrote:
>
>
>---
>You are receiving this because you are subscribed to this thread.
>Reply to this email directly or view it on GitHub:
>https://github.com/GaudiLabs/OpenDrop/issues/2

-- 
Sent from my Android device with K-9 Mail. Please excuse my brevity.

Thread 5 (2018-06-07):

### ISSUE TITLE
Droplets are not moving 

### ISSUE THREAD

**Issue by tomdertech** [GaudiLabs/OpenDrop#5]
Hi,

I have recreated stripped down opendrop (although at the moment I am using an external HV PSU). I do not have the screen and I have disabled the joystick. I have defined a start position `drop[0].begin(1,3)` and have set the code to loop between shifting right one position and then back left one position, however my droplet does not move.

**Testing & Setup**

Electrically I have proven that the voltage switches between the electrodes I expect. I have added a 3 second delay between each transition.

I have used Saran wrap pulled tight and held in position with double sided kapton tape. I have used a silicone oil on the electrodes and RainX (car windscreen repellant) as the hydrophobic coating on the droplet side of the saran wrap - you can see this here with the droplet.
![img_20170612_163716](https://user-images.githubusercontent.com/7968388/27042858-2014f864-4f90-11e7-9ff4-49b46facc956.jpg)

I have used ITO coated glass and used the copper tape method to connect to it. The conductive side is treated with RainX and faced down against the droplet with some tape to pack it. This can be seen here.
![img_20170612_163753](https://user-images.githubusercontent.com/7968388/27042916-5483d55c-4f90-11e7-8ded-b42062356096.jpg)

And when it is all together it looks like this
![img_20170612_164126](https://user-images.githubusercontent.com/7968388/27042937-6336a5ac-4f90-11e7-9f0d-98b0b05e73d5.jpg)

But the droplet does not move ... what should I try/am I missing?

Thanks.
Regards,
Tom

**Comment by GaudiLabs** [comment]
Follow the instructions here:
http://www.gaudi.ch/OpenDrop/?p=116
Urs

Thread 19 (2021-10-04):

### ISSUE TITLE
OpenDropController3_2 Compile Error

### ISSUE THREAD

**Issue by bhclowers** [GaudiLabs/OpenDrop#19]
Now that we are back in the lab we are trying to communicate with our OpenDrop v3.2 using the processing code.  We are using processing 4.0b1 and the OpenDropController3_2 from the github master.  When we try to compile we get the following error:

`frame cannot be resolved to a variable`

The associated tracebacks seems to point to line 138.  Looking at the code I don't see the variable defined either (but maybe I missed it).  Is it part of the javax.swing package and if so how to do we get that integrated?

Any help would be appreciated and I hope it is something simple.

Cheers.

**Comment by GaudiLabs** [comment]
frame is a special keyword as part of the showMessageDialog command. It does not need to be defined. This error message however suggests to me that something with your processing installation must be wrong. Try reinstalling the processing environment.

Best,
Urs

On 15 September 2021 20:48:59 CEST, bhclowers ***@***.***> wrote:
>Now that we are back in the lab we are trying to communicate with our OpenDrop v3.2 using the processing code.  We are using processing 4.0b1 and the OpenDropController3_2 from the github master.  When we try to compile we get the following error:
>
>`frame cannot be resolved to a variable`
>
>The associated tracebacks seems to point to line 138.  Looking at the code I don't see the variable defined either (but maybe I missed it).  Is it part of the javax.swing package and if so how to do we get that integrated?
>
>Any help would be appreciated and I hope it is something simple.
>
>Cheers.
>
>
>
>-- 
>You are receiving this because you are subscribed to this thread.
>Reply to this email directly or view it on GitHub:
>https://github.com/GaudiLabs/OpenDrop/issues/19
-- 
Sent from my Android device with K-9 Mail. Please excuse my brevity.

**Comment by bhclowers** [comment]
I just wanted to provide a follow-up.  This issue appears to be associated with the beta version of Processing 4.0b1. After trying multiple computers, it took me way too long to try out 3.5.  The older version of Processing worked fine.  In the release notes they highlight that processing moved from Java 8 to Java 11. I would guess that is the issue. Hope this helps someone else.

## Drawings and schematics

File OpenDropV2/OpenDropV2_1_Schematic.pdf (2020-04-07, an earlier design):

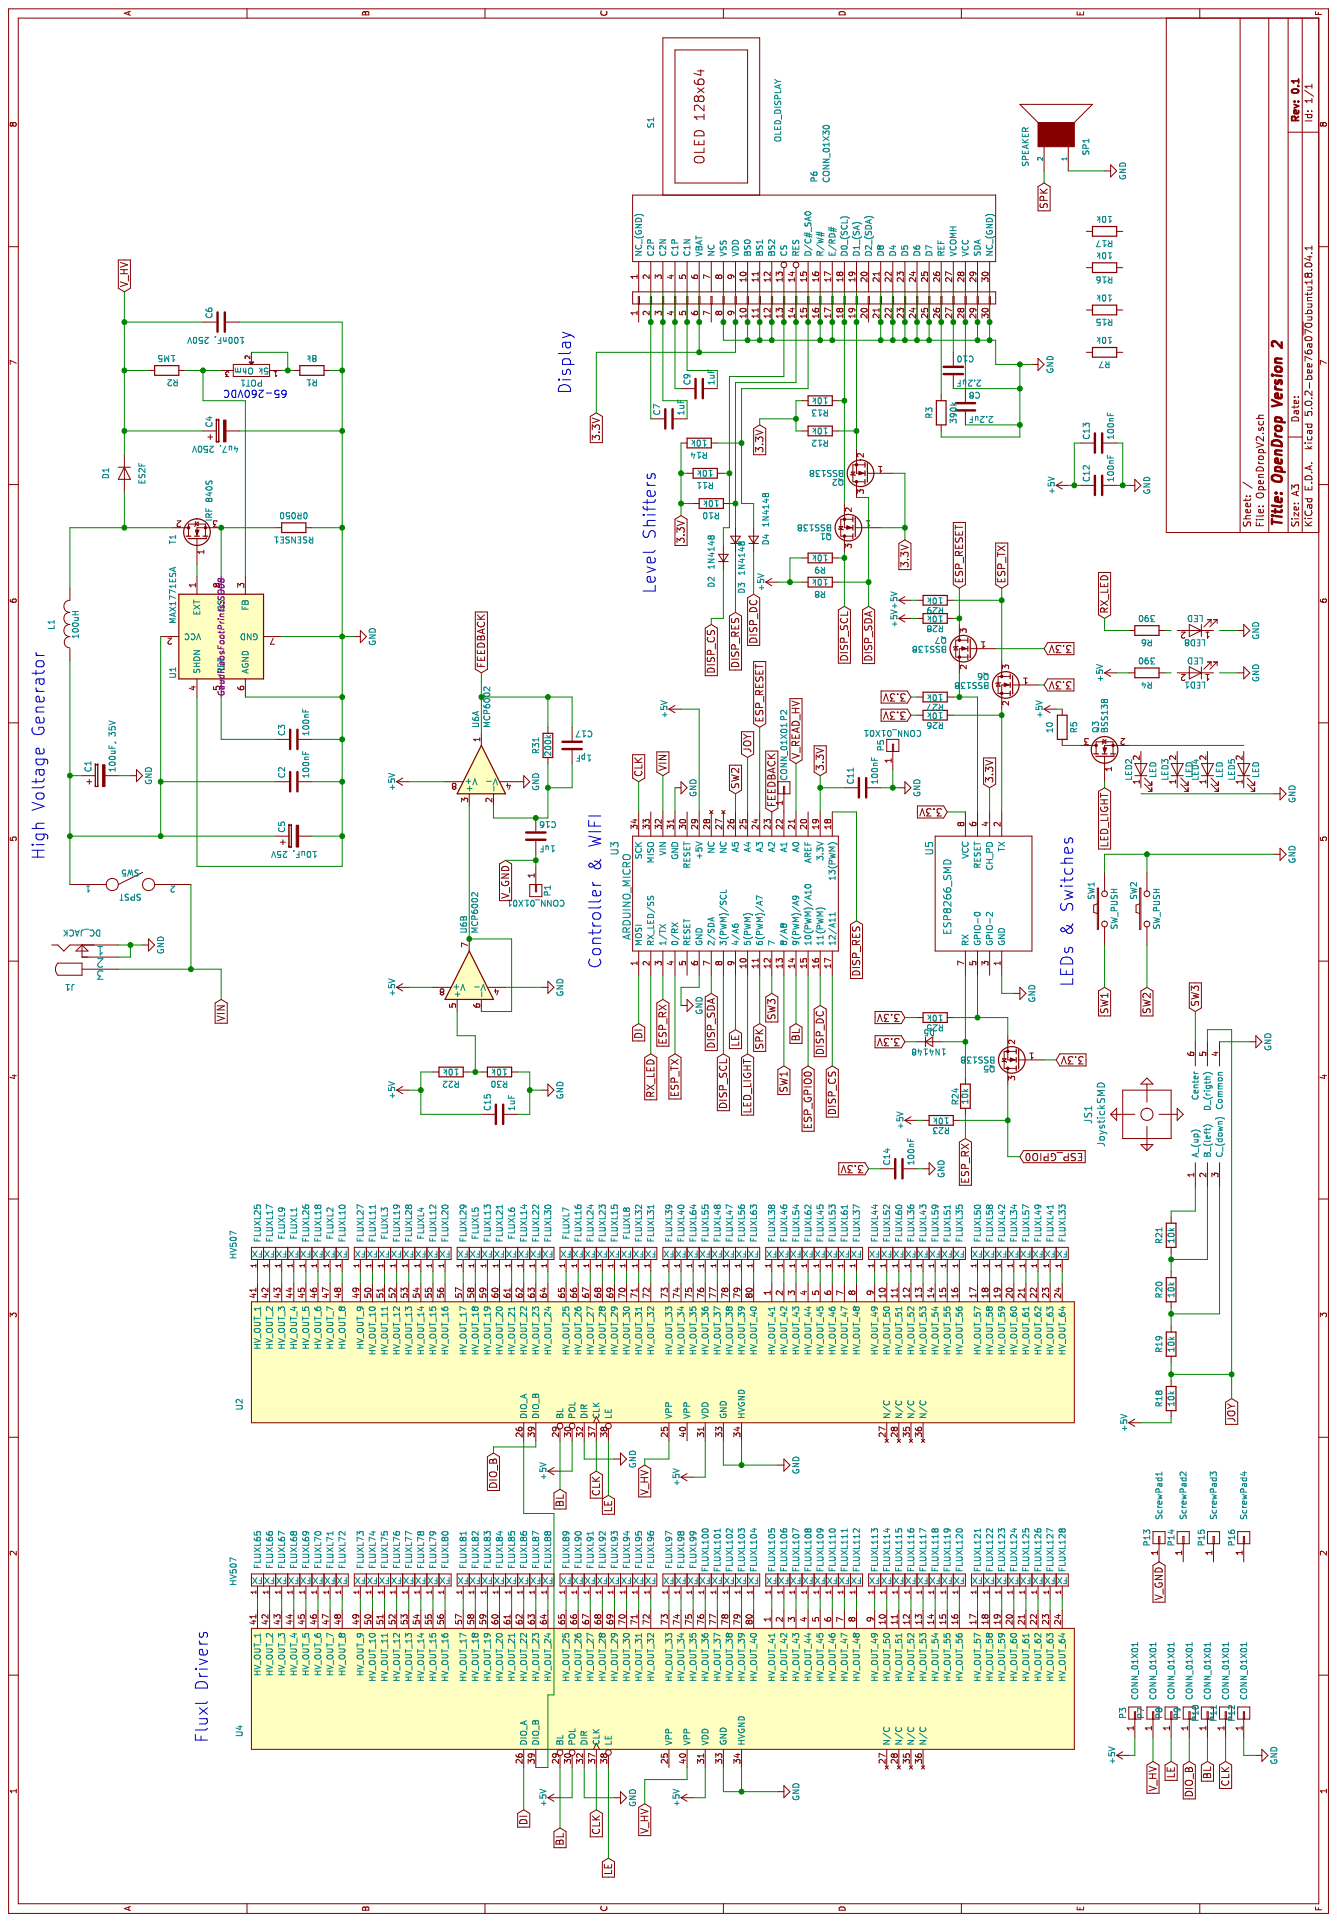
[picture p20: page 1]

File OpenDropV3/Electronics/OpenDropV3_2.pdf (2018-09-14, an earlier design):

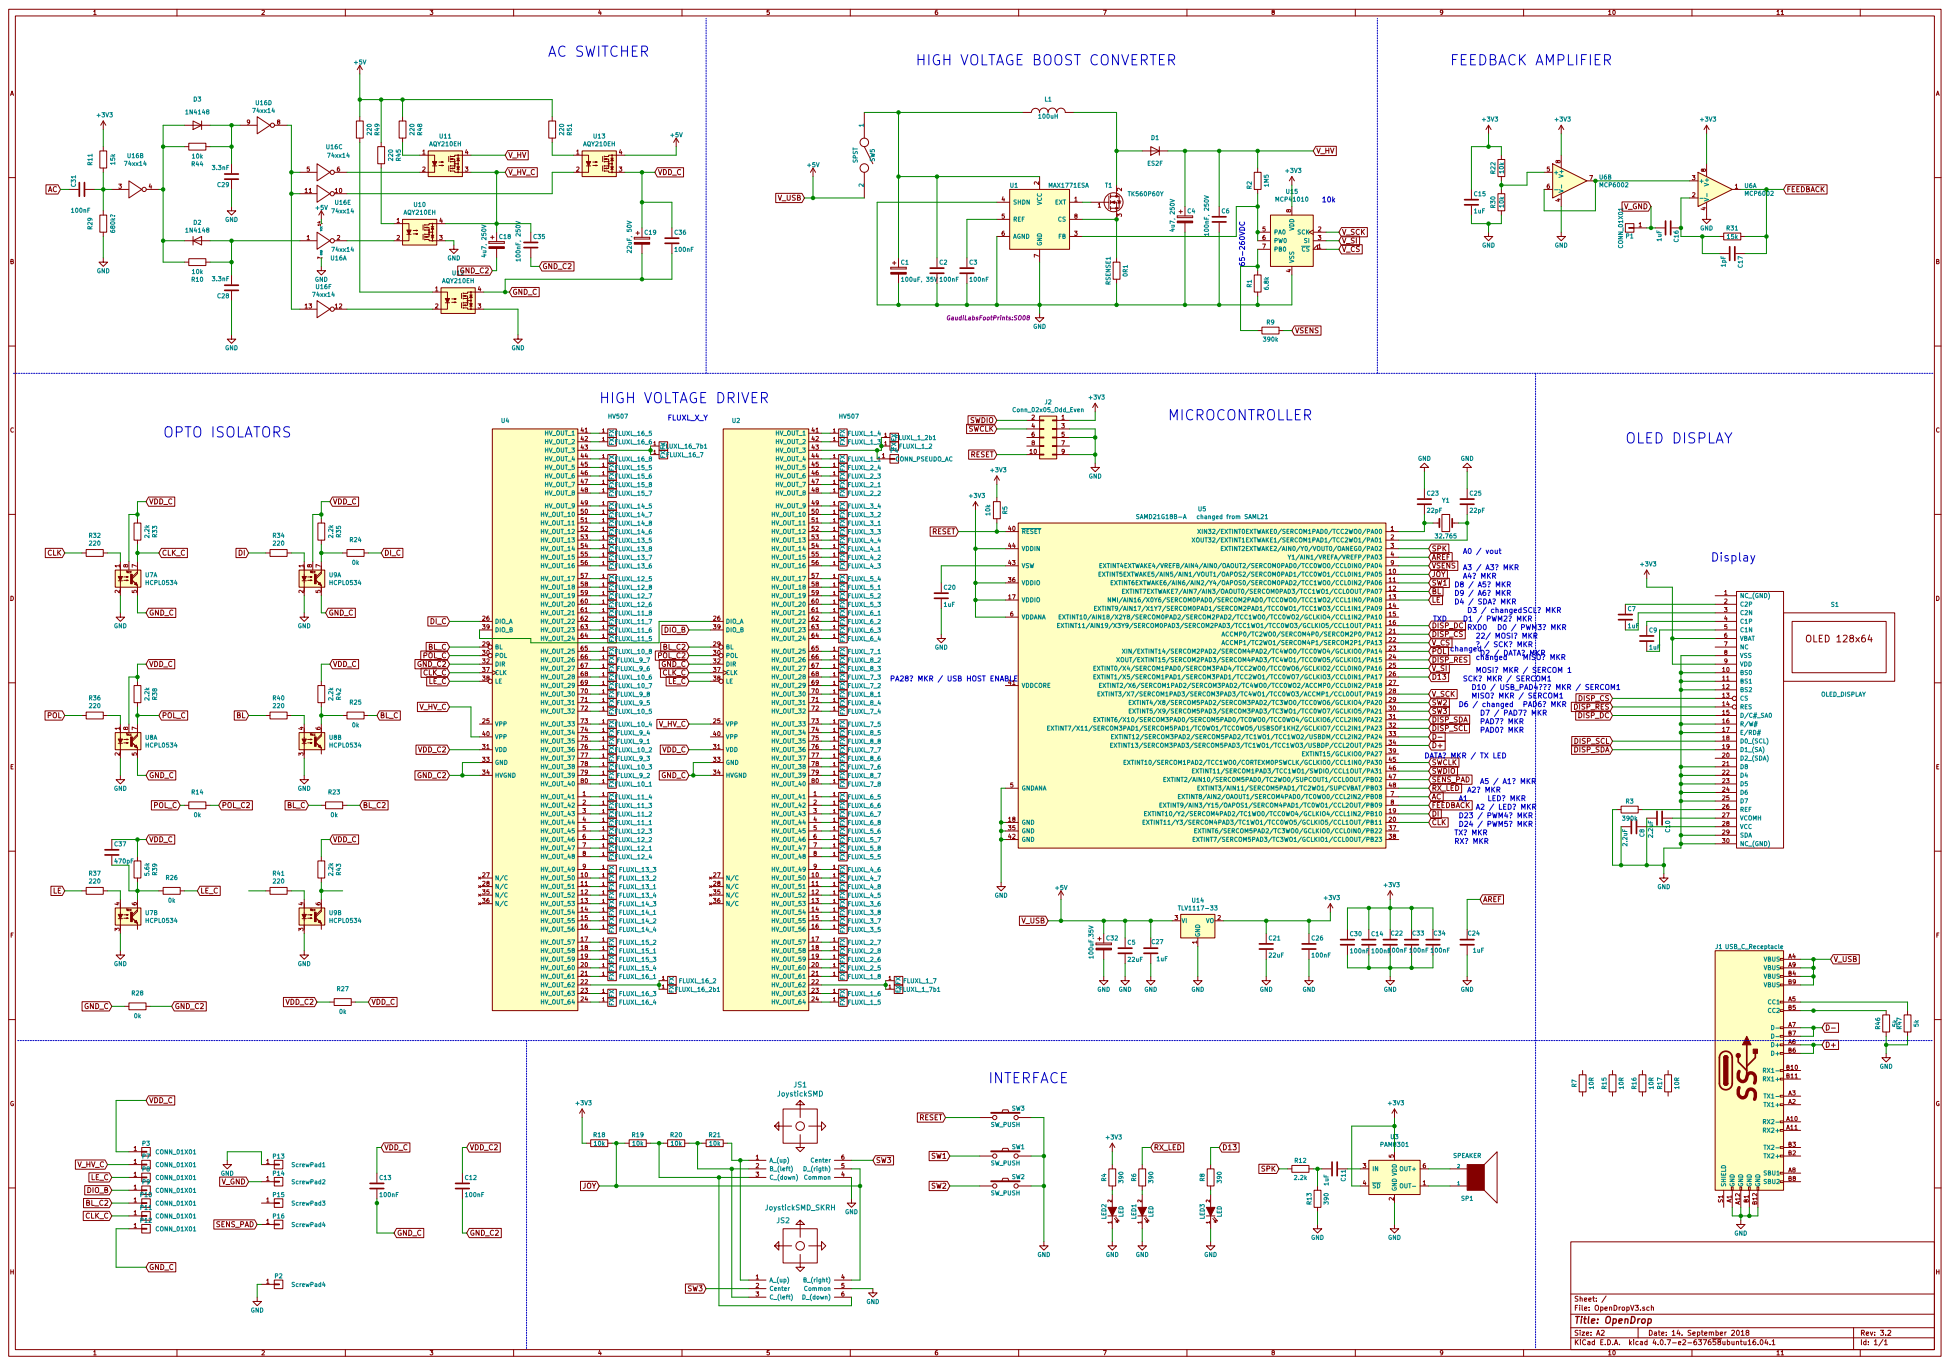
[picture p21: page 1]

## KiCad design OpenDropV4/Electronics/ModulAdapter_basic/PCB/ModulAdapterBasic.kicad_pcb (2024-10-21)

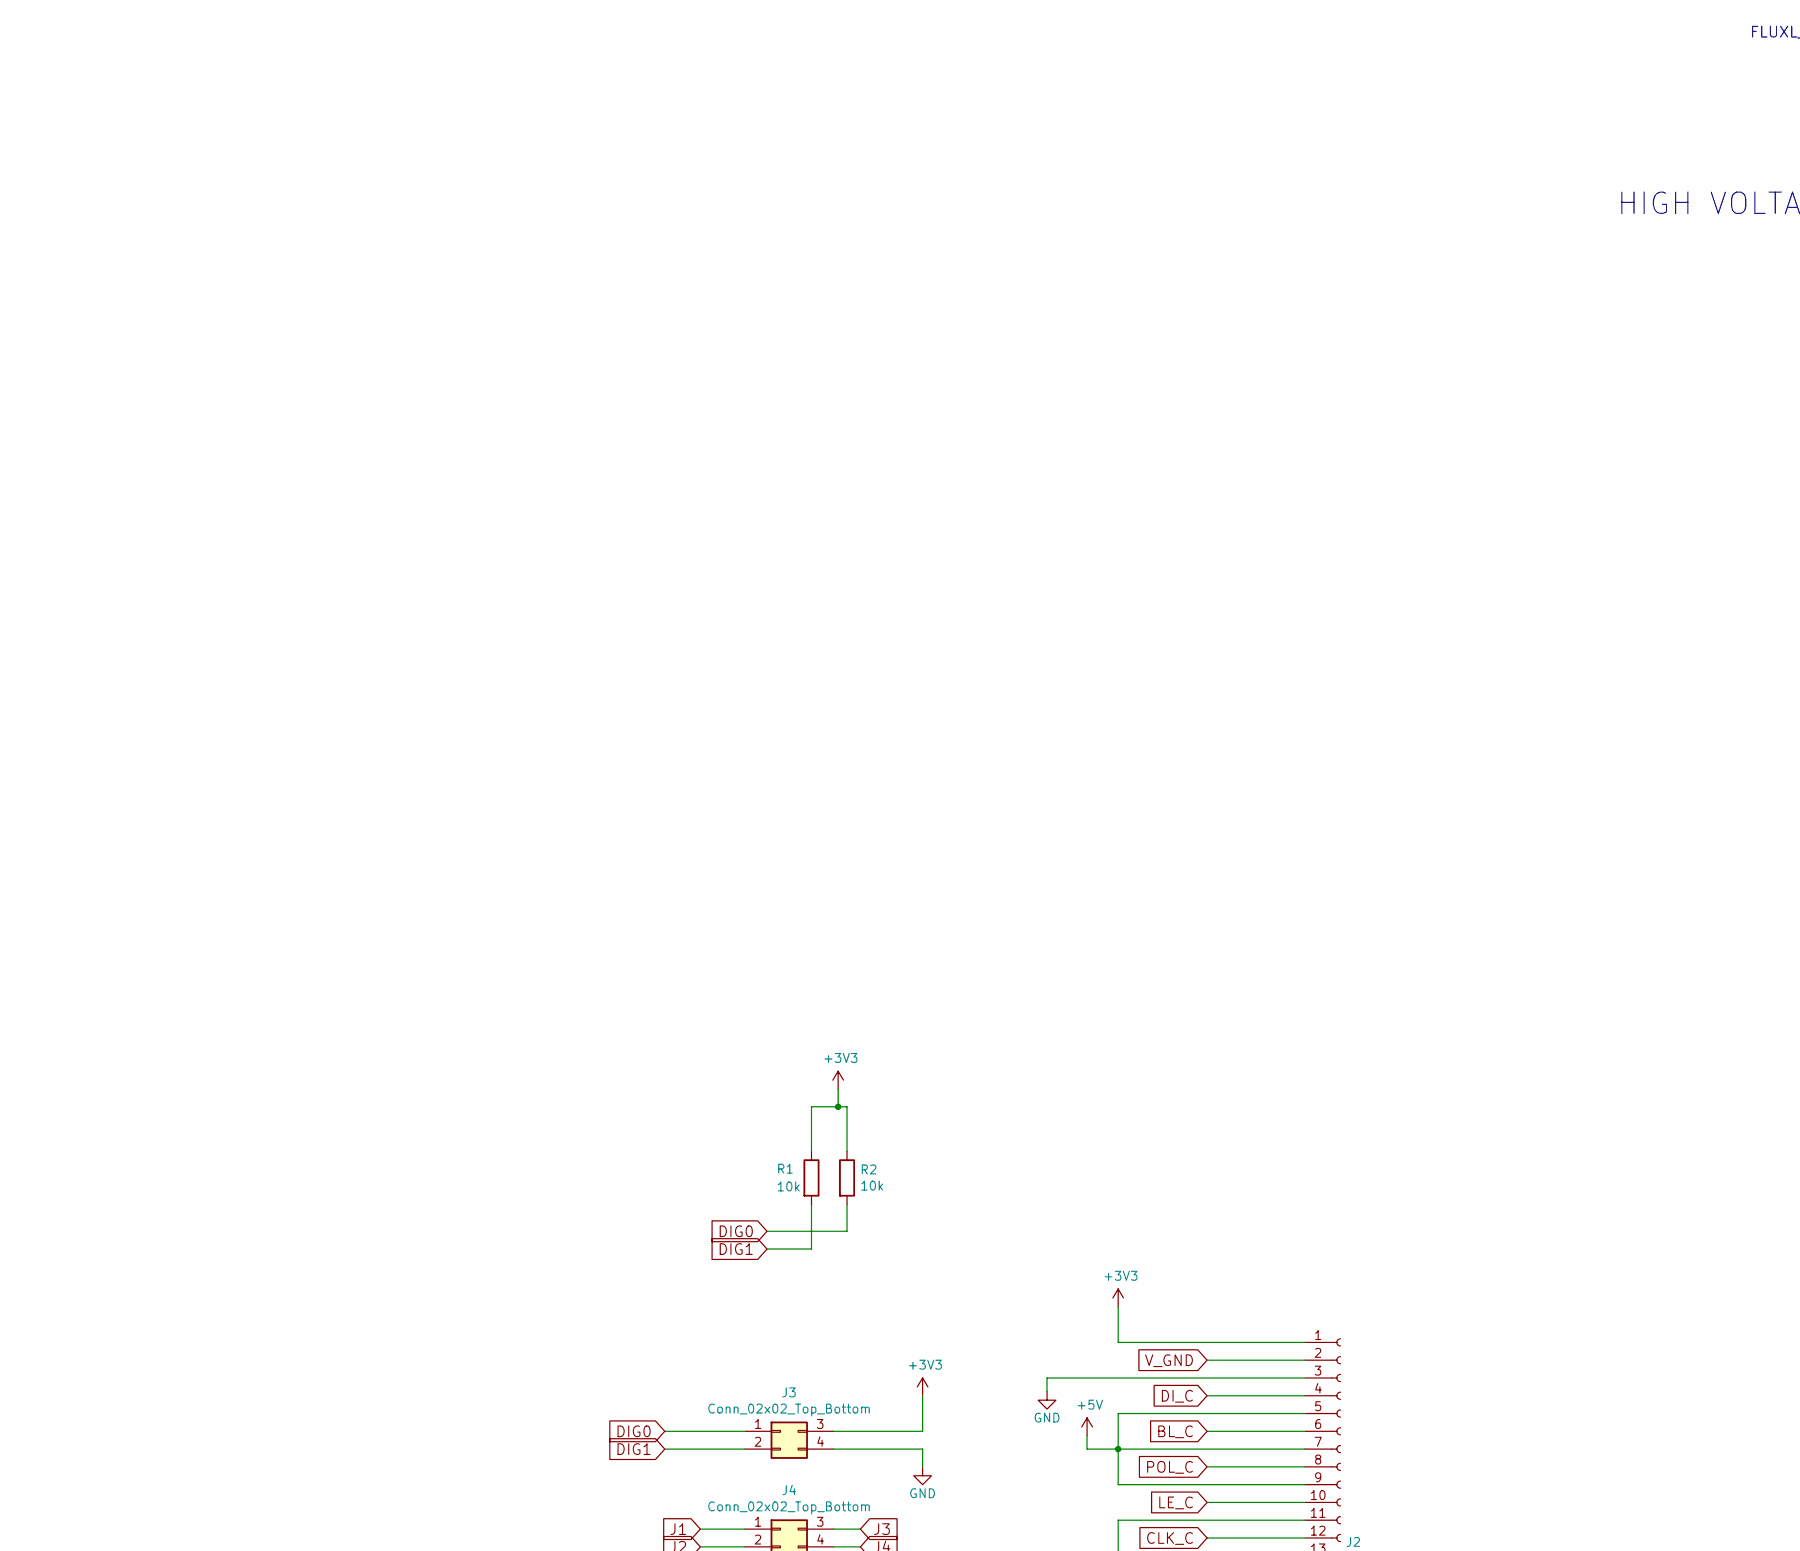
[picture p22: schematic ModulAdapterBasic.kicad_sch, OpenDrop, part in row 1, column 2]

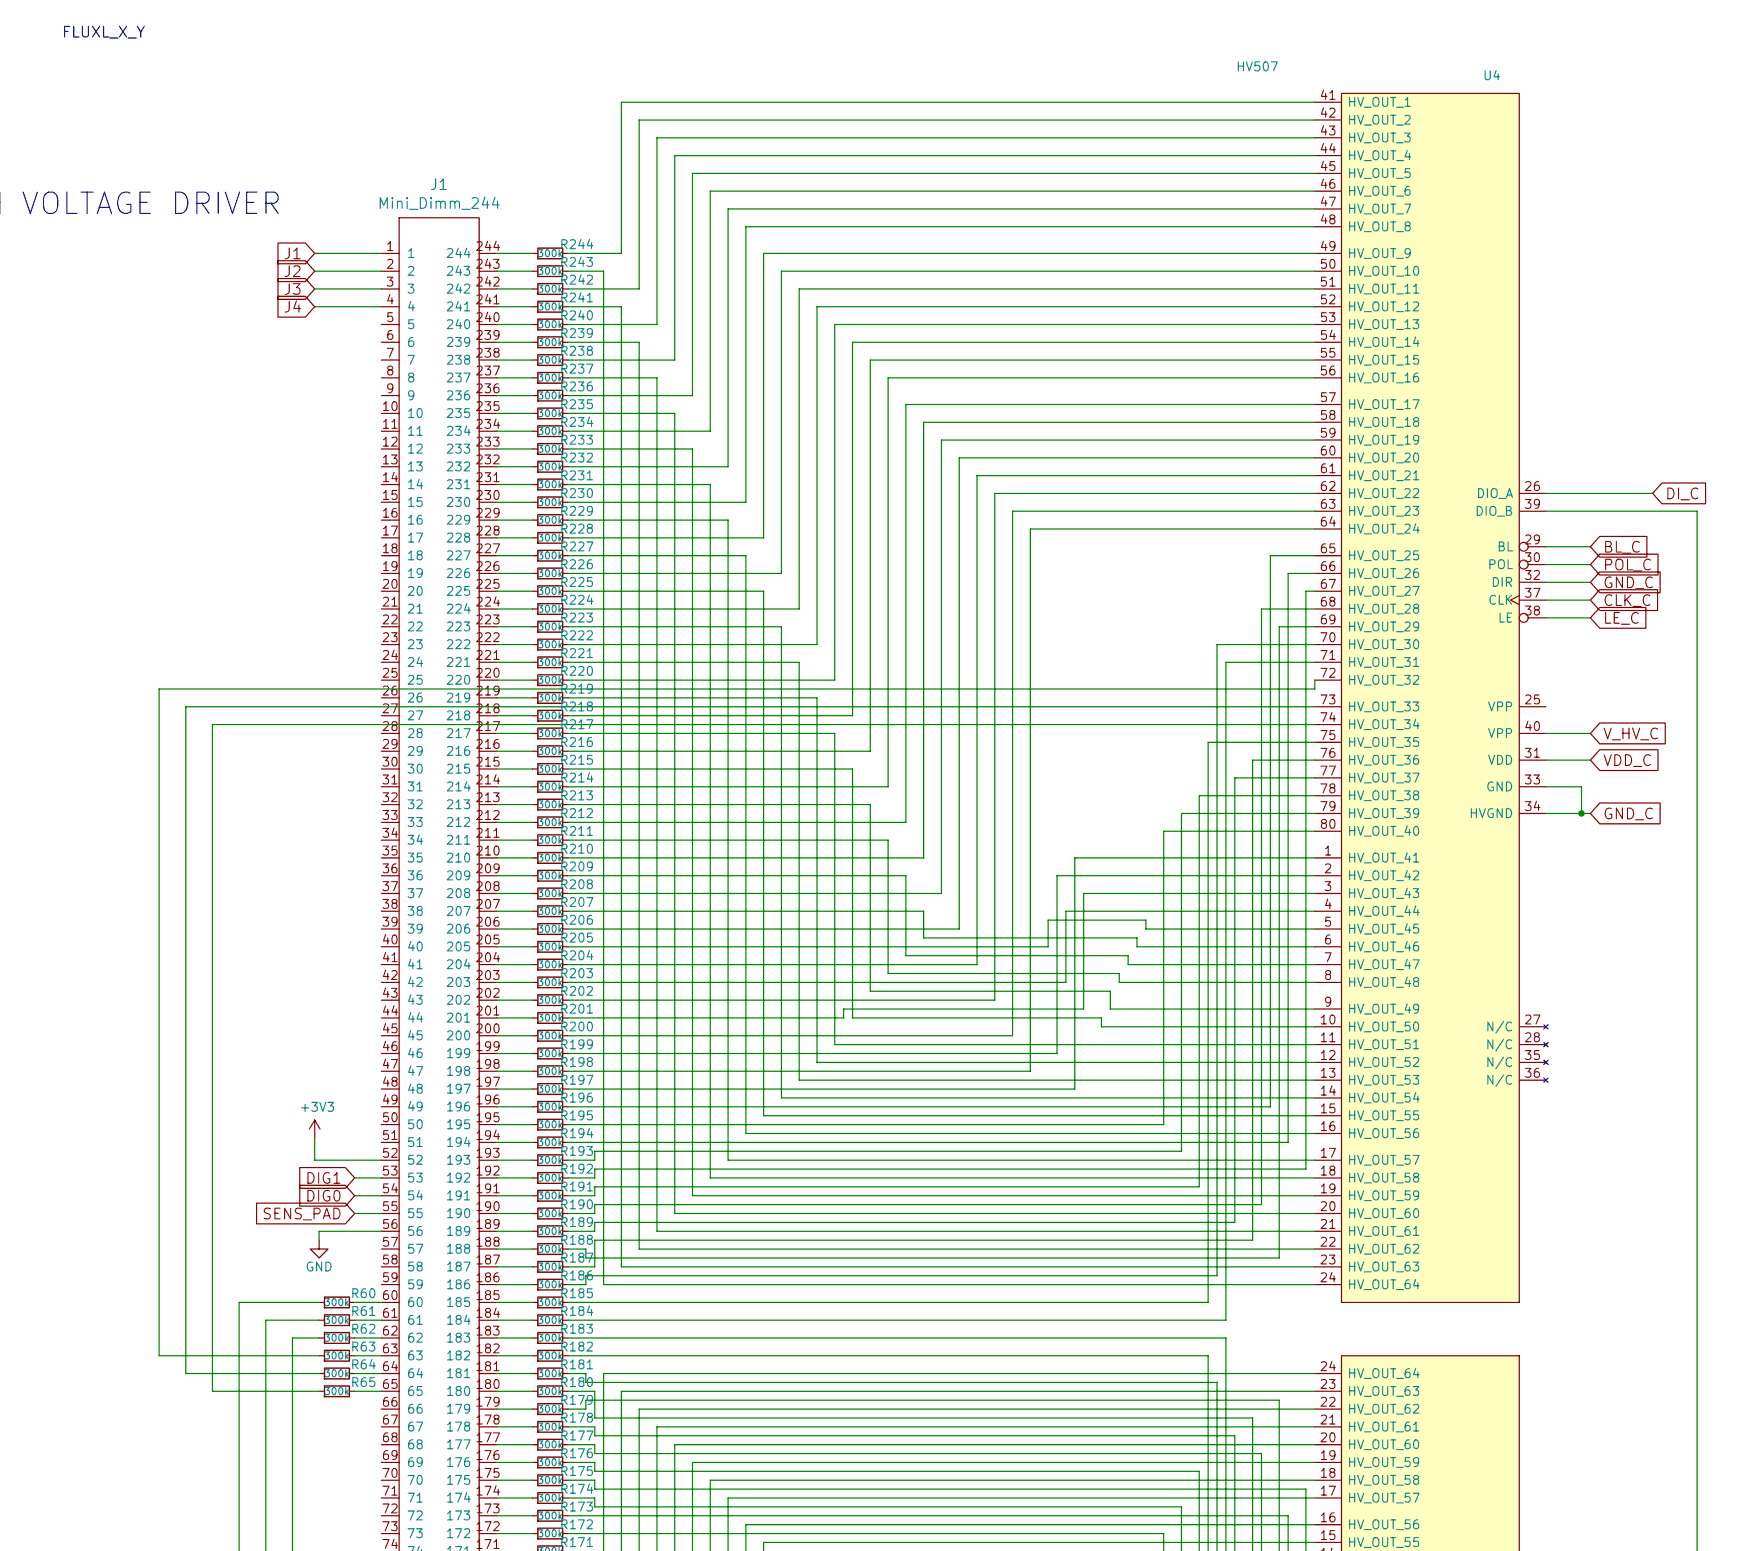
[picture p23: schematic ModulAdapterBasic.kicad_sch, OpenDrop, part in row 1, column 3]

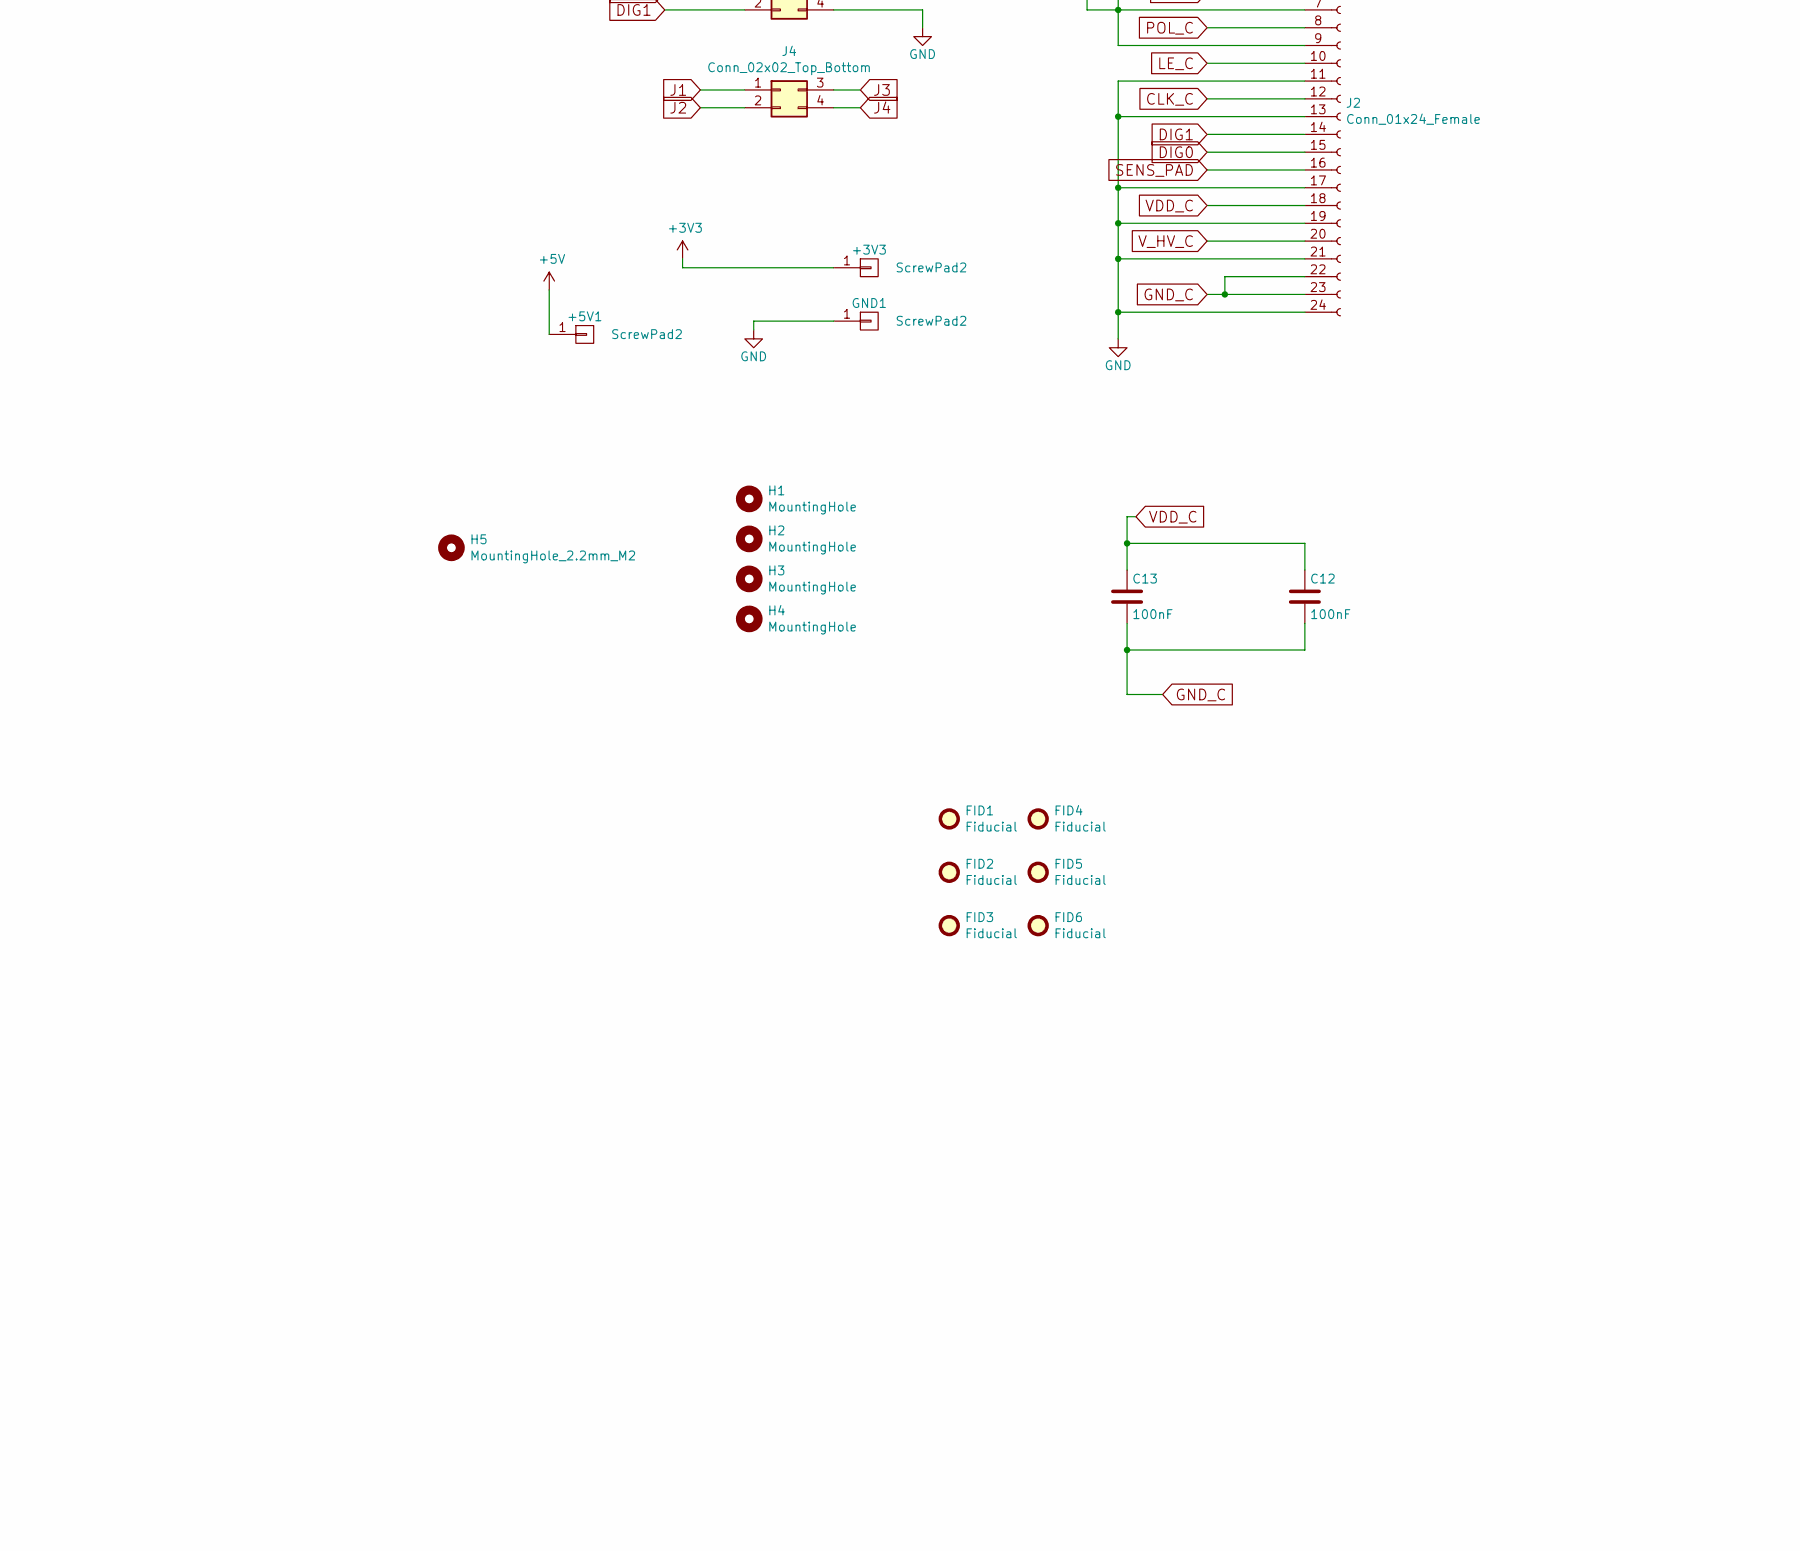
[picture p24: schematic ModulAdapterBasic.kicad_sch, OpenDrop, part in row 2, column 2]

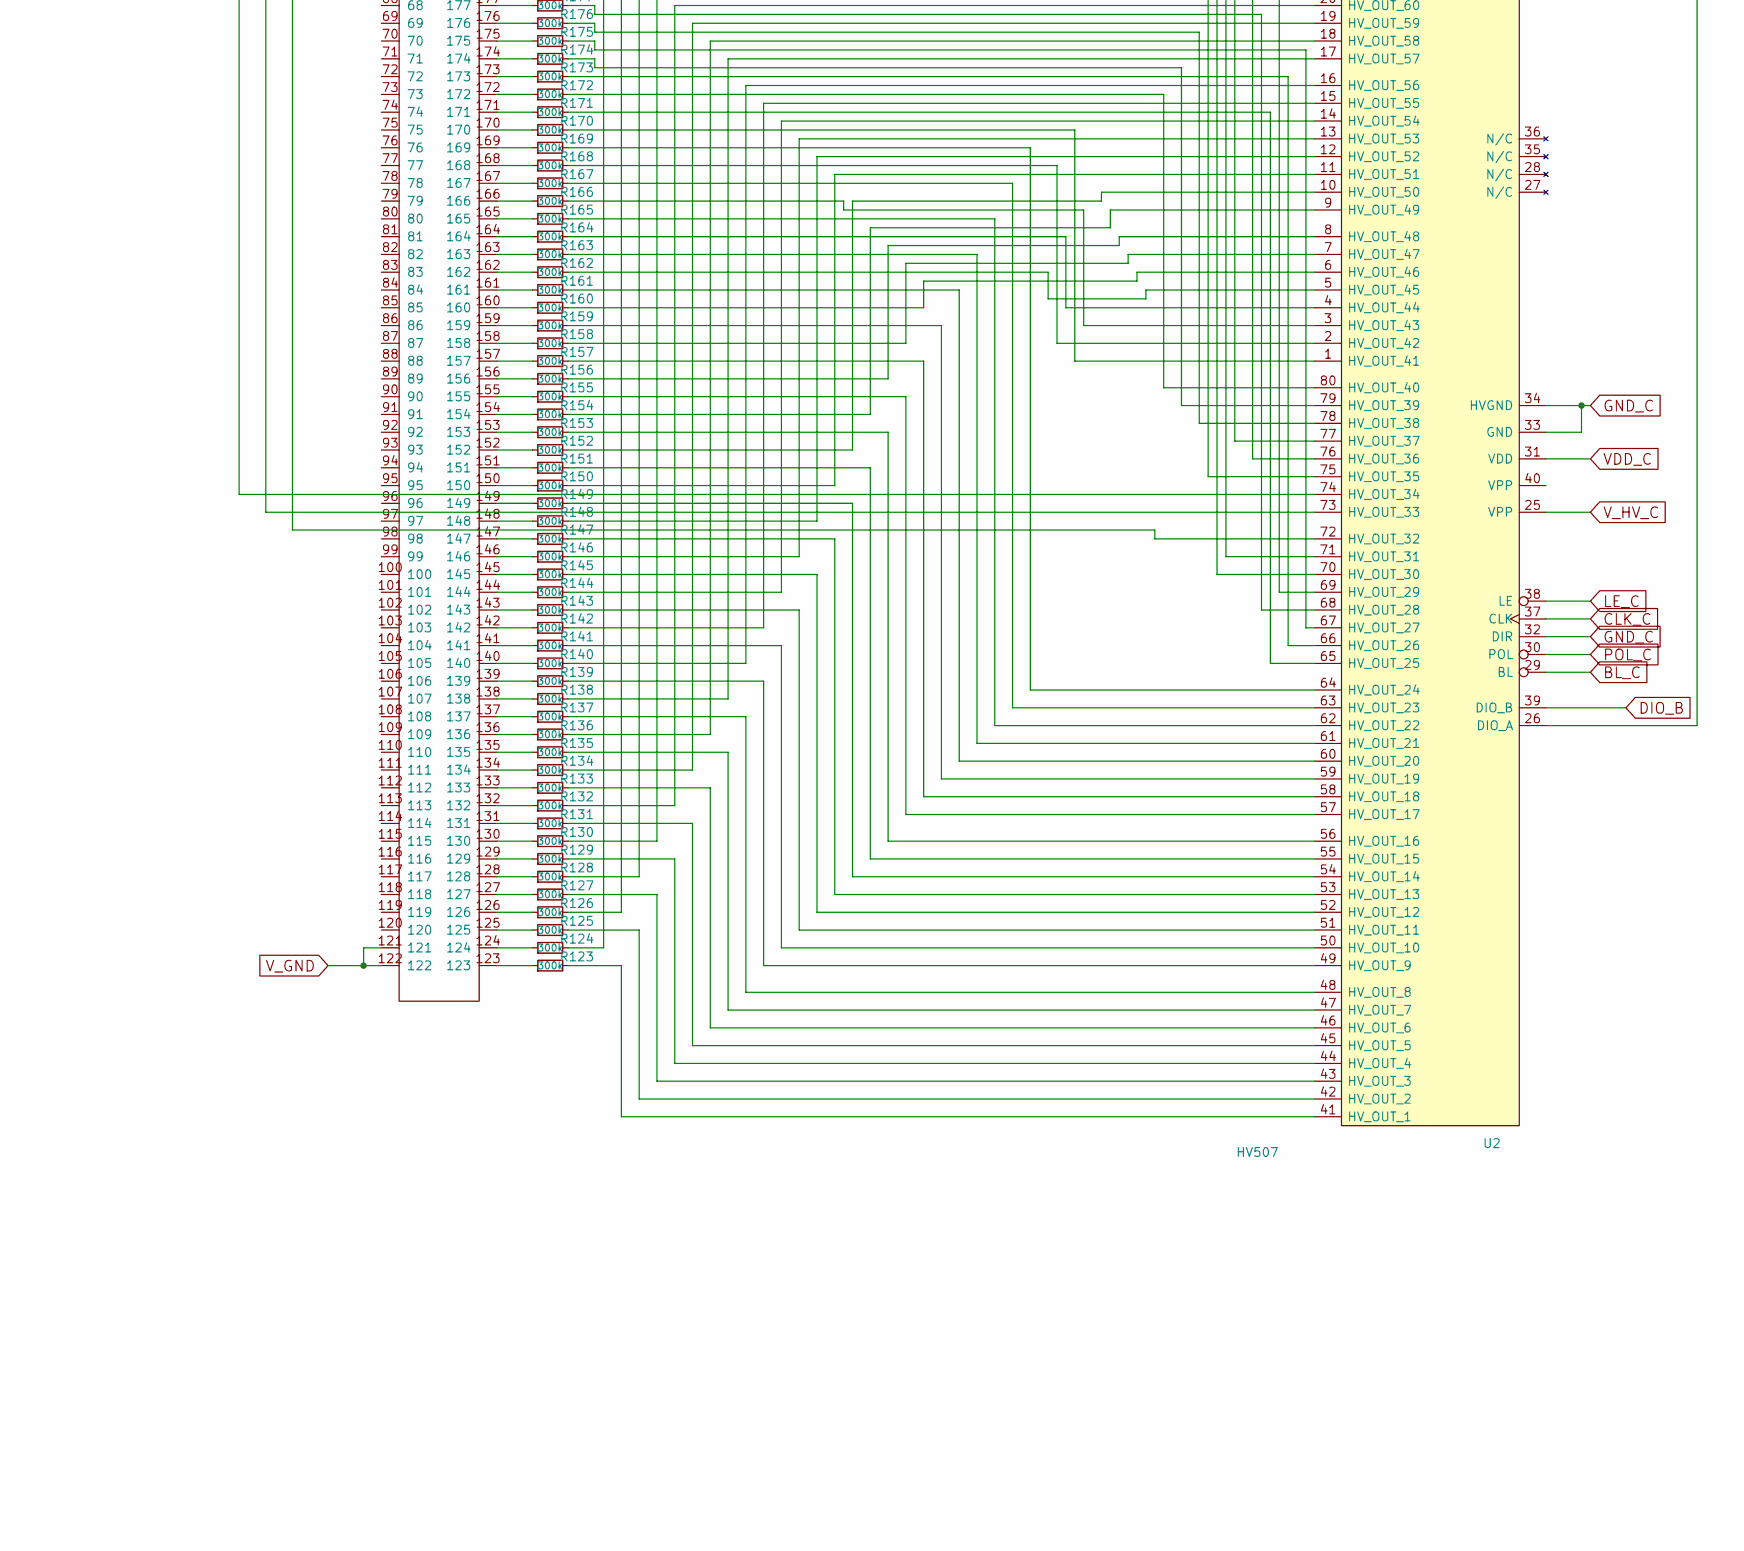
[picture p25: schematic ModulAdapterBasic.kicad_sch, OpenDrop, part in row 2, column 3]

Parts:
+3V3, +5V1: ScrewPad2; Measurement_Point_Square-SMD-Pad_Small
C12, C13: 100nF; C_0603_1608Metric
FID1, FID2, FID3, FID4, FID5, FID6: Fiducial; Fiducial_1mm_Dia_2.54mm_Outer_CopperBottom
GND1: ScrewPad2; Measurement_Point_Square-SMD-Pad_Small
H1, H2, H3, H4: MountingHole; MountingHoleM3
H5: MountingHole_2.2mm_M2
J1: Mini_Dimm_244; MiniDimm_06_244_200
J2: Conn_01x24_Female; FFC_MOLEX_EASYON_05mm_24
J3, J4: Conn_02x02_Top_Bottom; PinHeader_2x02_P2.00mm_Vertical
R1, R2: 10k; R_0603_1608Metric
R60, R61, R62, R63, R64, R65, R123, R124, R125, R126, R127, R128, R129, R130, R131, R132, R133, R134, R135, R136, R137, R138, R139, R140, R141, R142, R143, R144, R145, R146, R147, R148, R149, R150, R151, R152, R153, R154, R155, R156, R157, R158, R159, R160, R161, R162, R163, R164, R165, R166, R167, R168, R169, R170, R171, R172, R173, R174, R175, R176, R177, R178, R179, R180, R181, R182, R183, R184, R185, R186, R187, R188, R189, R190, R191, R192, R193, R194, R195, R196, R197, R198, R199, R200, R201, R202, R203, R204, R205, R206, R207, R208, R209, R210, R211, R212, R213, R214, R215, R216, R217, R218, R219, R220, R221, R222, R223, R224, R225, R226, R227, R228, R229, R230, R231, R232, R233, R234, R235, R236, R237, R238, R239, R240, R241, R242, R243, R244: 300k; R_0402_1005Metric
U2, U4: HV507; PQFP-80_14x20mm_Pitch0.8mm

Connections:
+3V3: +3V3.1, J1.52, J2.1, J3.3, R1.1, R2.1
+5V: +5V1.1, J2.5, J2.7, J2.9
BL_C: J2.6, U2.29 (BL), U4.29 (BL)
CLK_C: J2.12, U2.37 (CLK), U4.37 (CLK)
DIG0: J1.54, J2.15, J3.1, R2.2
DIG1: J1.53, J2.14, J3.2, R1.2
DIO_B: U2.39 (DIO_B)
DI_C: J2.4, U4.26 (DIO_A)
GND: GND1.1, J1.56, J2.3, J2.11, J2.13, J2.17, J2.19, J2.21, J2.24, J3.4
GND_C: C12.2, C13.2, J2.22, J2.23, U2.32 (DIR), U2.33 (GND), U2.34 (HVGND), U4.32 (DIR), U4.33 (GND), U4.34 (HVGND)
J1: J1.1, J4.1
J2: J1.2, J4.2
J3: J1.3, J4.3
J4: J1.4, J4.4
LE_C: J2.10, U2.38 (LE), U4.38 (LE)
unnamed: J1.60, R60.2
unnamed: J1.61, R61.2
unnamed: J1.62, R62.2
unnamed: J1.63, R63.2
unnamed: J1.64, R64.2
unnamed: J1.65, R65.2
unnamed: J1.123, R123.1
unnamed: J1.124, R124.1
unnamed: J1.125, R125.1
unnamed: J1.126, R126.1
unnamed: J1.127, R127.1
unnamed: J1.128, R128.1
unnamed: J1.129, R129.1
unnamed: J1.130, R130.1
unnamed: J1.131, R131.1
unnamed: J1.132, R132.1
unnamed: J1.133, R133.1
unnamed: J1.134, R134.1
unnamed: J1.135, R135.1
unnamed: J1.136, R136.1
unnamed: J1.137, R137.1
unnamed: J1.138, R138.1
unnamed: J1.139, R139.1
unnamed: J1.140, R140.1
unnamed: J1.141, R141.1
unnamed: J1.142, R142.1
unnamed: J1.143, R143.1
unnamed: J1.144, R144.1
unnamed: J1.145, R145.1
unnamed: J1.146, R146.1
unnamed: J1.147, R147.1
unnamed: J1.148, R148.1
unnamed: J1.149, R149.1
unnamed: J1.150, R150.1
unnamed: J1.151, R151.1
unnamed: J1.152, R152.1
unnamed: J1.153, R153.1
unnamed: J1.154, R154.1
unnamed: J1.155, R155.1
unnamed: J1.156, R156.1
unnamed: J1.157, R157.1
unnamed: J1.158, R158.1
unnamed: J1.159, R159.1
unnamed: J1.160, R160.1
unnamed: J1.161, R161.1
unnamed: J1.162, R162.1
unnamed: J1.163, R163.1
unnamed: J1.164, R164.1
unnamed: J1.165, R165.1
unnamed: J1.166, R166.1
unnamed: J1.167, R167.1
unnamed: J1.168, R168.1
unnamed: J1.169, R169.1
unnamed: J1.170, R170.1
unnamed: J1.171, R171.1
unnamed: J1.172, R172.1
unnamed: J1.173, R173.1
unnamed: J1.174, R174.1
unnamed: J1.175, R175.1
unnamed: J1.176, R176.1
unnamed: J1.177, R177.1
unnamed: J1.178, R178.1
unnamed: J1.179, R179.1
unnamed: J1.180, R180.1
unnamed: J1.181, R181.1
unnamed: J1.182, R182.1
unnamed: J1.183, R183.1
unnamed: J1.184, R184.1
unnamed: J1.185, R185.1
unnamed: J1.186, R186.1
unnamed: J1.187, R187.1
unnamed: J1.188, R188.1
unnamed: J1.189, R189.1
unnamed: J1.190, R190.1
unnamed: J1.191, R191.1
unnamed: J1.192, R192.1
unnamed: J1.193, R193.1
unnamed: J1.194, R194.1
unnamed: J1.195, R195.1
unnamed: J1.196, R196.1
unnamed: J1.197, R197.1
unnamed: J1.198, R198.1
unnamed: J1.199, R199.1
unnamed: J1.200, R200.1
unnamed: J1.201, R201.1
unnamed: J1.202, R202.1
unnamed: J1.203, R203.1
unnamed: J1.204, R204.1
unnamed: J1.205, R205.1
unnamed: J1.206, R206.1
unnamed: J1.207, R207.1
unnamed: J1.208, R208.1
unnamed: J1.209, R209.1
unnamed: J1.210, R210.1
unnamed: J1.211, R211.1
unnamed: J1.212, R212.1
unnamed: J1.213, R213.1
unnamed: J1.214, R214.1
unnamed: J1.215, R215.1
unnamed: J1.216, R216.1
unnamed: J1.217, R217.1
unnamed: J1.218, R218.1
unnamed: J1.219, R219.1
unnamed: J1.220, R220.1
unnamed: J1.221, R221.1
unnamed: J1.222, R222.1
unnamed: J1.223, R223.1
unnamed: J1.224, R224.1
unnamed: J1.225, R225.1
unnamed: J1.226, R226.1
unnamed: J1.227, R227.1
unnamed: J1.228, R228.1
unnamed: J1.229, R229.1
unnamed: J1.230, R230.1
unnamed: J1.231, R231.1
unnamed: J1.232, R232.1
unnamed: J1.233, R233.1
unnamed: J1.234, R234.1
unnamed: J1.235, R235.1
unnamed: J1.236, R236.1
unnamed: J1.237, R237.1
unnamed: J1.238, R238.1
unnamed: J1.239, R239.1
unnamed: J1.240, R240.1
unnamed: J1.241, R241.1
unnamed: J1.242, R242.1
unnamed: J1.243, R243.1
unnamed: J1.244, R244.1
unnamed: R60.1, U2.74 (HV_OUT_34)
unnamed: R61.1, U2.73 (HV_OUT_33)
unnamed: R62.1, U2.72 (HV_OUT_32)
unnamed: R63.1, U4.72 (HV_OUT_32)
unnamed: R64.1, U4.73 (HV_OUT_33)
unnamed: R65.1, U4.74 (HV_OUT_34)
unnamed: R123.2, U2.41 (HV_OUT_1)
unnamed: R124.2, U2.24 (HV_OUT_64)
unnamed: R125.2, U2.42 (HV_OUT_2)
unnamed: R126.2, U2.23 (HV_OUT_63)
unnamed: R127.2, U2.43 (HV_OUT_3)
unnamed: R128.2, U2.22 (HV_OUT_62)
unnamed: R129.2, U2.44 (HV_OUT_4)
unnamed: R130.2, U2.21 (HV_OUT_61)
unnamed: R131.2, U2.45 (HV_OUT_5)
unnamed: R132.2, U2.20 (HV_OUT_60)
unnamed: R133.2, U2.46 (HV_OUT_6)
unnamed: R134.2, U2.19 (HV_OUT_59)
unnamed: R135.2, U2.47 (HV_OUT_7)
unnamed: R136.2, U2.18 (HV_OUT_58)
unnamed: R137.2, U2.48 (HV_OUT_8)
unnamed: R138.2, U2.17 (HV_OUT_57)
unnamed: R139.2, U2.49 (HV_OUT_9)
unnamed: R140.2, U2.16 (HV_OUT_56)
unnamed: R141.2, U2.50 (HV_OUT_10)
unnamed: R142.2, U2.15 (HV_OUT_55)
unnamed: R143.2, U2.51 (HV_OUT_11)
unnamed: R144.2, U2.14 (HV_OUT_54)
unnamed: R145.2, U2.52 (HV_OUT_12)
unnamed: R146.2, U2.13 (HV_OUT_53)
unnamed: R147.2, U2.53 (HV_OUT_13)
unnamed: R148.2, U2.12 (HV_OUT_52)
unnamed: R149.2, U2.54 (HV_OUT_14)
unnamed: R150.2, U2.11 (HV_OUT_51)
unnamed: R151.2, U2.55 (HV_OUT_15)
unnamed: R152.2, U2.10 (HV_OUT_50)
unnamed: R153.2, U2.56 (HV_OUT_16)
unnamed: R154.2, U2.9 (HV_OUT_49)
unnamed: R155.2, U2.57 (HV_OUT_17)
unnamed: R156.2, U2.8 (HV_OUT_48)
unnamed: R157.2, U2.58 (HV_OUT_18)
unnamed: R158.2, U2.7 (HV_OUT_47)
unnamed: R159.2, U2.59 (HV_OUT_19)
unnamed: R160.2, U2.6 (HV_OUT_46)
unnamed: R161.2, U2.60 (HV_OUT_20)
unnamed: R162.2, U2.5 (HV_OUT_45)
unnamed: R163.2, U2.61 (HV_OUT_21)
unnamed: R164.2, U2.4 (HV_OUT_44)
unnamed: R165.2, U2.62 (HV_OUT_22)
unnamed: R166.2, U2.3 (HV_OUT_43)
unnamed: R167.2, U2.63 (HV_OUT_23)
unnamed: R168.2, U2.2 (HV_OUT_42)
unnamed: R169.2, U2.64 (HV_OUT_24)
unnamed: R170.2, U2.1 (HV_OUT_41)
unnamed: R171.2, U2.65 (HV_OUT_25)
unnamed: R172.2, U2.80 (HV_OUT_40)
unnamed: R173.2, U2.66 (HV_OUT_26)
unnamed: R174.2, U2.79 (HV_OUT_39)
unnamed: R175.2, U2.67 (HV_OUT_27)
unnamed: R176.2, U2.78 (HV_OUT_38)
unnamed: R177.2, U2.68 (HV_OUT_28)
unnamed: R178.2, U2.77 (HV_OUT_37)
unnamed: R179.2, U2.69 (HV_OUT_29)
unnamed: R180.2, U2.76 (HV_OUT_36)
unnamed: R181.2, U2.70 (HV_OUT_30)
unnamed: R182.2, U2.75 (HV_OUT_35)
unnamed: R183.2, U2.71 (HV_OUT_31)
unnamed: R184.2, U4.71 (HV_OUT_31)
unnamed: R185.2, U4.75 (HV_OUT_35)
unnamed: R186.2, U4.70 (HV_OUT_30)
unnamed: R187.2, U4.76 (HV_OUT_36)
unnamed: R188.2, U4.69 (HV_OUT_29)
unnamed: R189.2, U4.77 (HV_OUT_37)
unnamed: R190.2, U4.68 (HV_OUT_28)
unnamed: R191.2, U4.78 (HV_OUT_38)
unnamed: R192.2, U4.67 (HV_OUT_27)
unnamed: R193.2, U4.79 (HV_OUT_39)
unnamed: R194.2, U4.66 (HV_OUT_26)
unnamed: R195.2, U4.80 (HV_OUT_40)
unnamed: R196.2, U4.65 (HV_OUT_25)
unnamed: R197.2, U4.1 (HV_OUT_41)
unnamed: R198.2, U4.64 (HV_OUT_24)
unnamed: R199.2, U4.2 (HV_OUT_42)
unnamed: R200.2, U4.63 (HV_OUT_23)
unnamed: R201.2, U4.3 (HV_OUT_43)
unnamed: R202.2, U4.62 (HV_OUT_22)
unnamed: R203.2, U4.4 (HV_OUT_44)
unnamed: R204.2, U4.61 (HV_OUT_21)
unnamed: R205.2, U4.5 (HV_OUT_45)
unnamed: R206.2, U4.60 (HV_OUT_20)
unnamed: R207.2, U4.6 (HV_OUT_46)
unnamed: R208.2, U4.59 (HV_OUT_19)
unnamed: R209.2, U4.7 (HV_OUT_47)
unnamed: R210.2, U4.58 (HV_OUT_18)
unnamed: R211.2, U4.8 (HV_OUT_48)
unnamed: R212.2, U4.57 (HV_OUT_17)
unnamed: R213.2, U4.9 (HV_OUT_49)
unnamed: R214.2, U4.56 (HV_OUT_16)
unnamed: R215.2, U4.10 (HV_OUT_50)
unnamed: R216.2, U4.55 (HV_OUT_15)
unnamed: R217.2, U4.11 (HV_OUT_51)
unnamed: R218.2, U4.54 (HV_OUT_14)
unnamed: R219.2, U4.12 (HV_OUT_52)
unnamed: R220.2, U4.53 (HV_OUT_13)
unnamed: R221.2, U4.13 (HV_OUT_53)
unnamed: R222.2, U4.52 (HV_OUT_12)
unnamed: R223.2, U4.14 (HV_OUT_54)
unnamed: R224.2, U4.51 (HV_OUT_11)
unnamed: R225.2, U4.15 (HV_OUT_55)
unnamed: R226.2, U4.50 (HV_OUT_10)
unnamed: R227.2, U4.16 (HV_OUT_56)
unnamed: R228.2, U4.49 (HV_OUT_9)
unnamed: R229.2, U4.17 (HV_OUT_57)
unnamed: R230.2, U4.48 (HV_OUT_8)
unnamed: R231.2, U4.18 (HV_OUT_58)
unnamed: R232.2, U4.47 (HV_OUT_7)
unnamed: R233.2, U4.19 (HV_OUT_59)
unnamed: R234.2, U4.46 (HV_OUT_6)
unnamed: R235.2, U4.20 (HV_OUT_60)
unnamed: R236.2, U4.45 (HV_OUT_5)
unnamed: R237.2, U4.21 (HV_OUT_61)
unnamed: R238.2, U4.44 (HV_OUT_4)
unnamed: R239.2, U4.22 (HV_OUT_62)
unnamed: R240.2, U4.43 (HV_OUT_3)
unnamed: R241.2, U4.23 (HV_OUT_63)
unnamed: R242.2, U4.42 (HV_OUT_2)
unnamed: R243.2, U4.24 (HV_OUT_64)
unnamed: R244.2, U4.41 (HV_OUT_1)
unnamed: U2.26 (DIO_A), U4.39 (DIO_B)
POL_C: J2.8, U2.30 (POL), U4.30 (POL)
SENS_PAD: J1.55, J2.16
VDD_C: C12.1, C13.1, J2.18, U2.31 (VDD), U4.31 (VDD)
V_GND: J1.121, J1.122, J2.2
V_HV_C: J2.20, U2.25 (VPP), U4.40 (VPP)

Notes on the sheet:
FLUXL_X_Y
HIGH VOLTAGE DRIVER

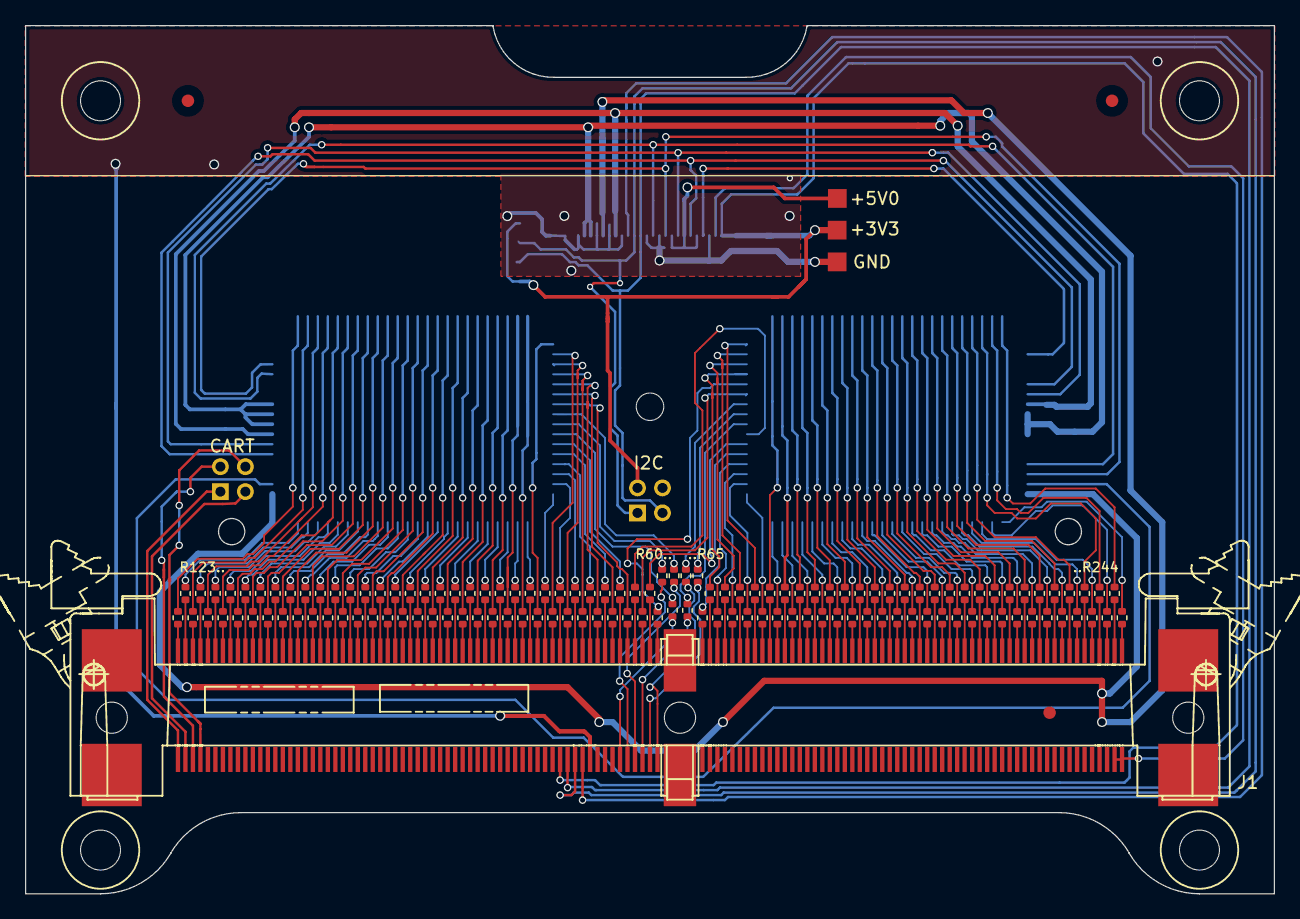
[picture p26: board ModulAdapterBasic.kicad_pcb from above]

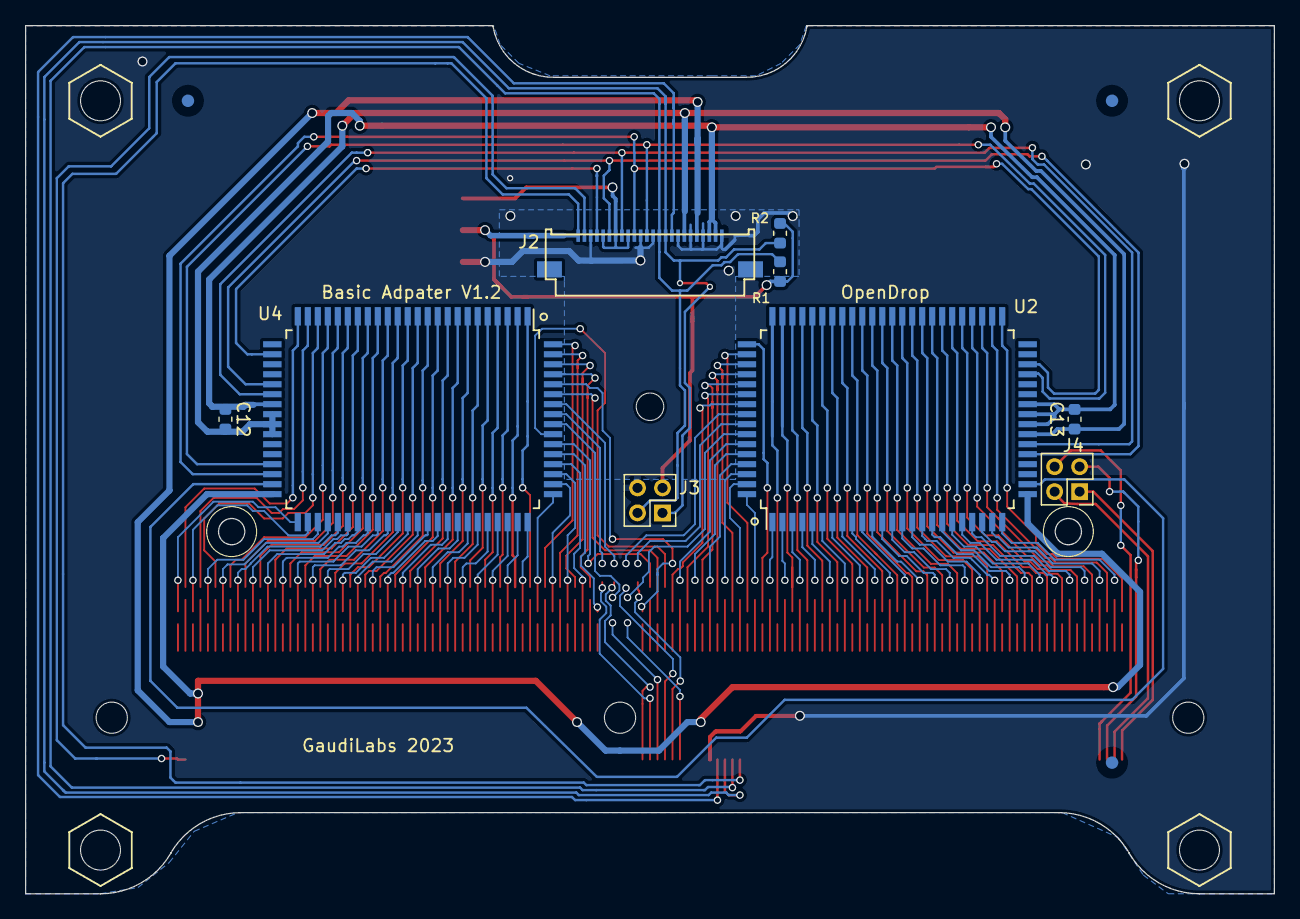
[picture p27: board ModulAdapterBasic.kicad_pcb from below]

Board: 2 copper layers, 100.0 x 69.5 mm, 152 parts (12 on the bottom side), 276 nets.

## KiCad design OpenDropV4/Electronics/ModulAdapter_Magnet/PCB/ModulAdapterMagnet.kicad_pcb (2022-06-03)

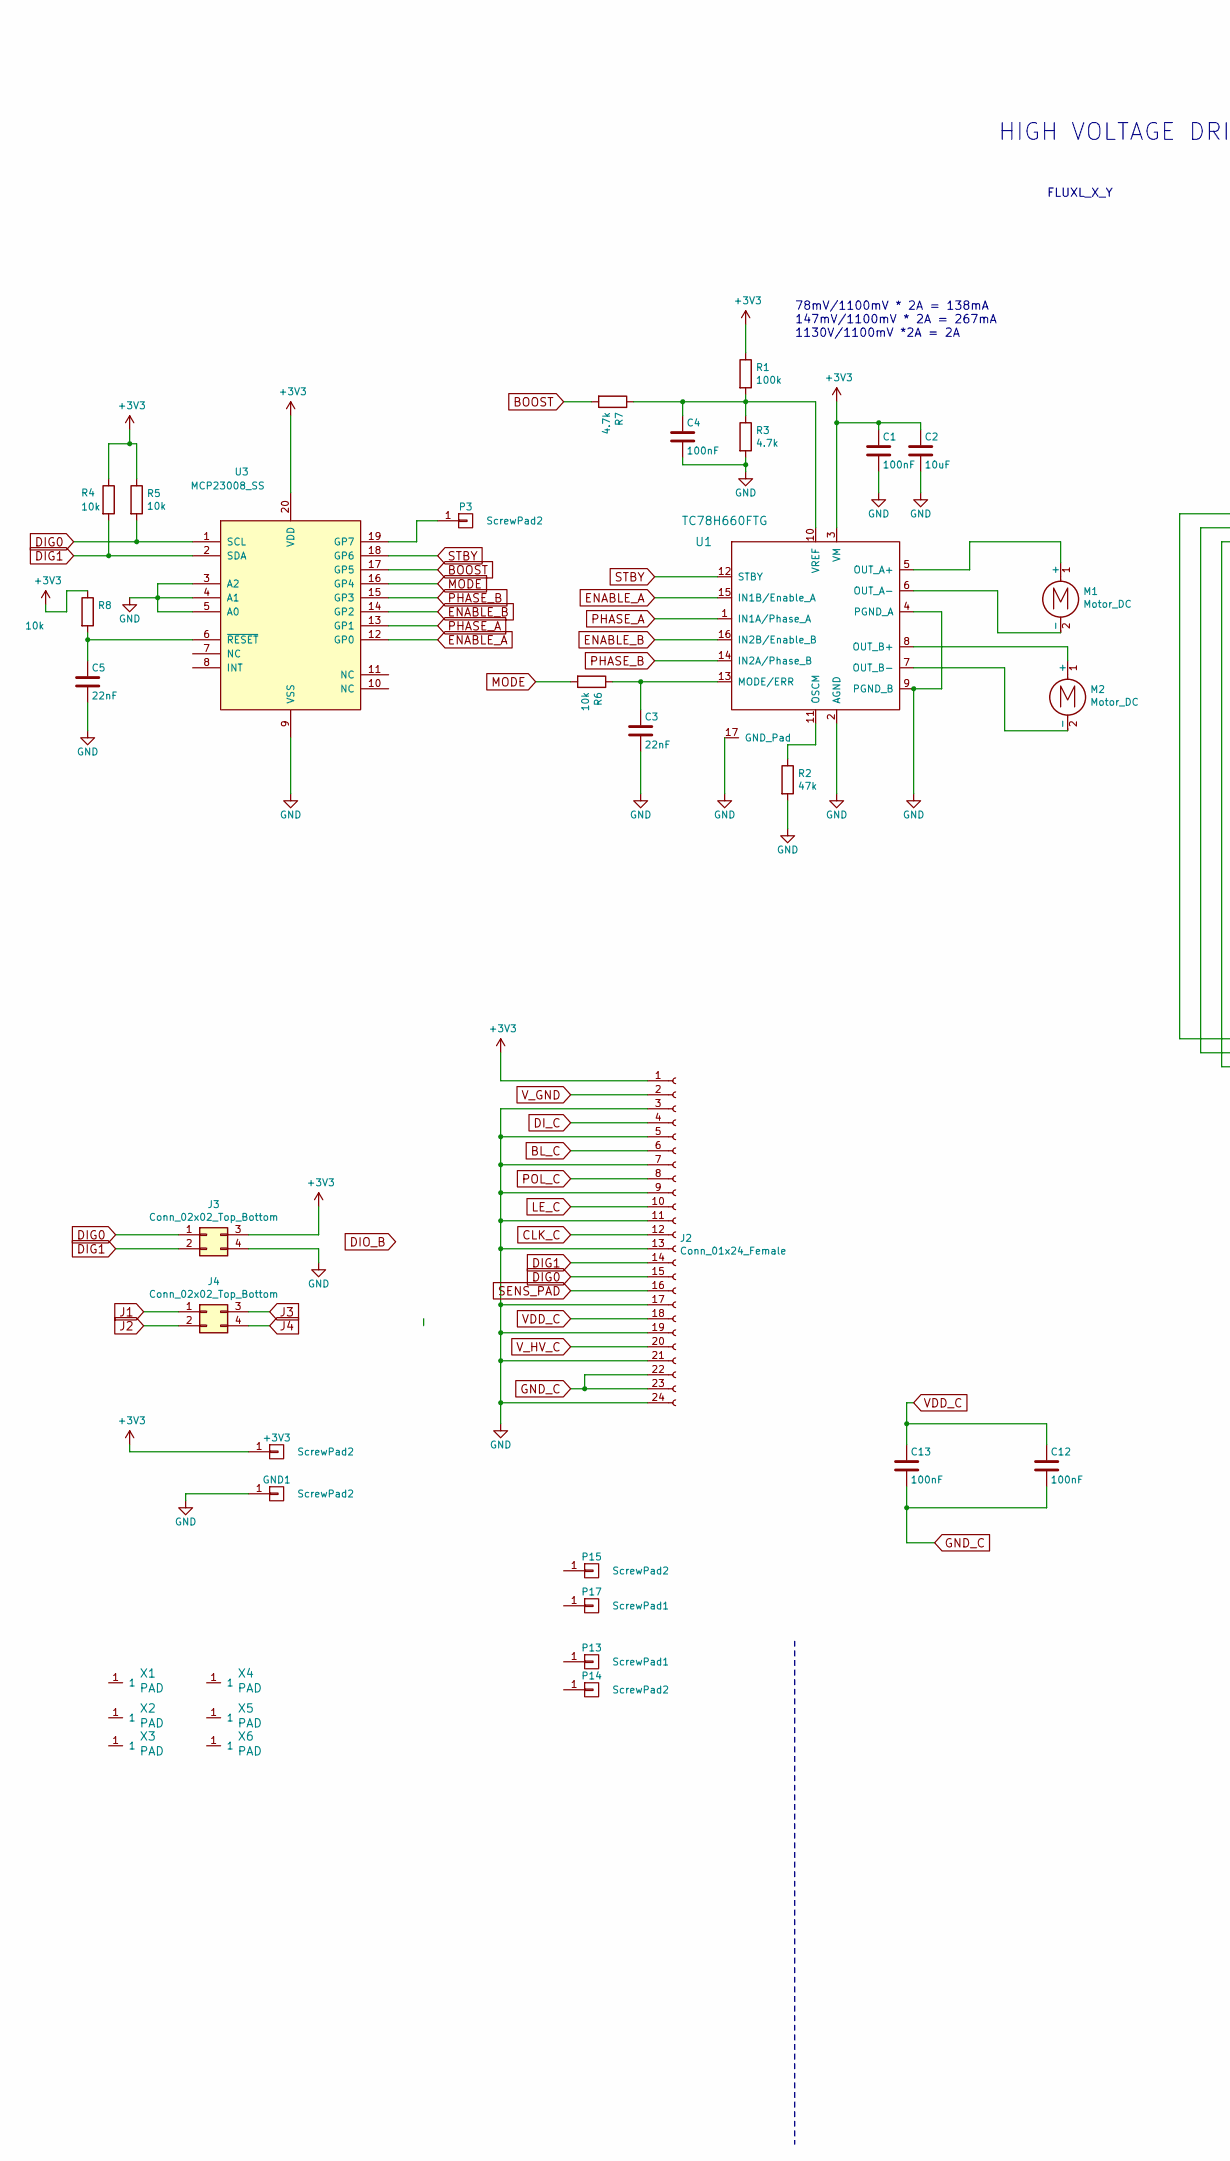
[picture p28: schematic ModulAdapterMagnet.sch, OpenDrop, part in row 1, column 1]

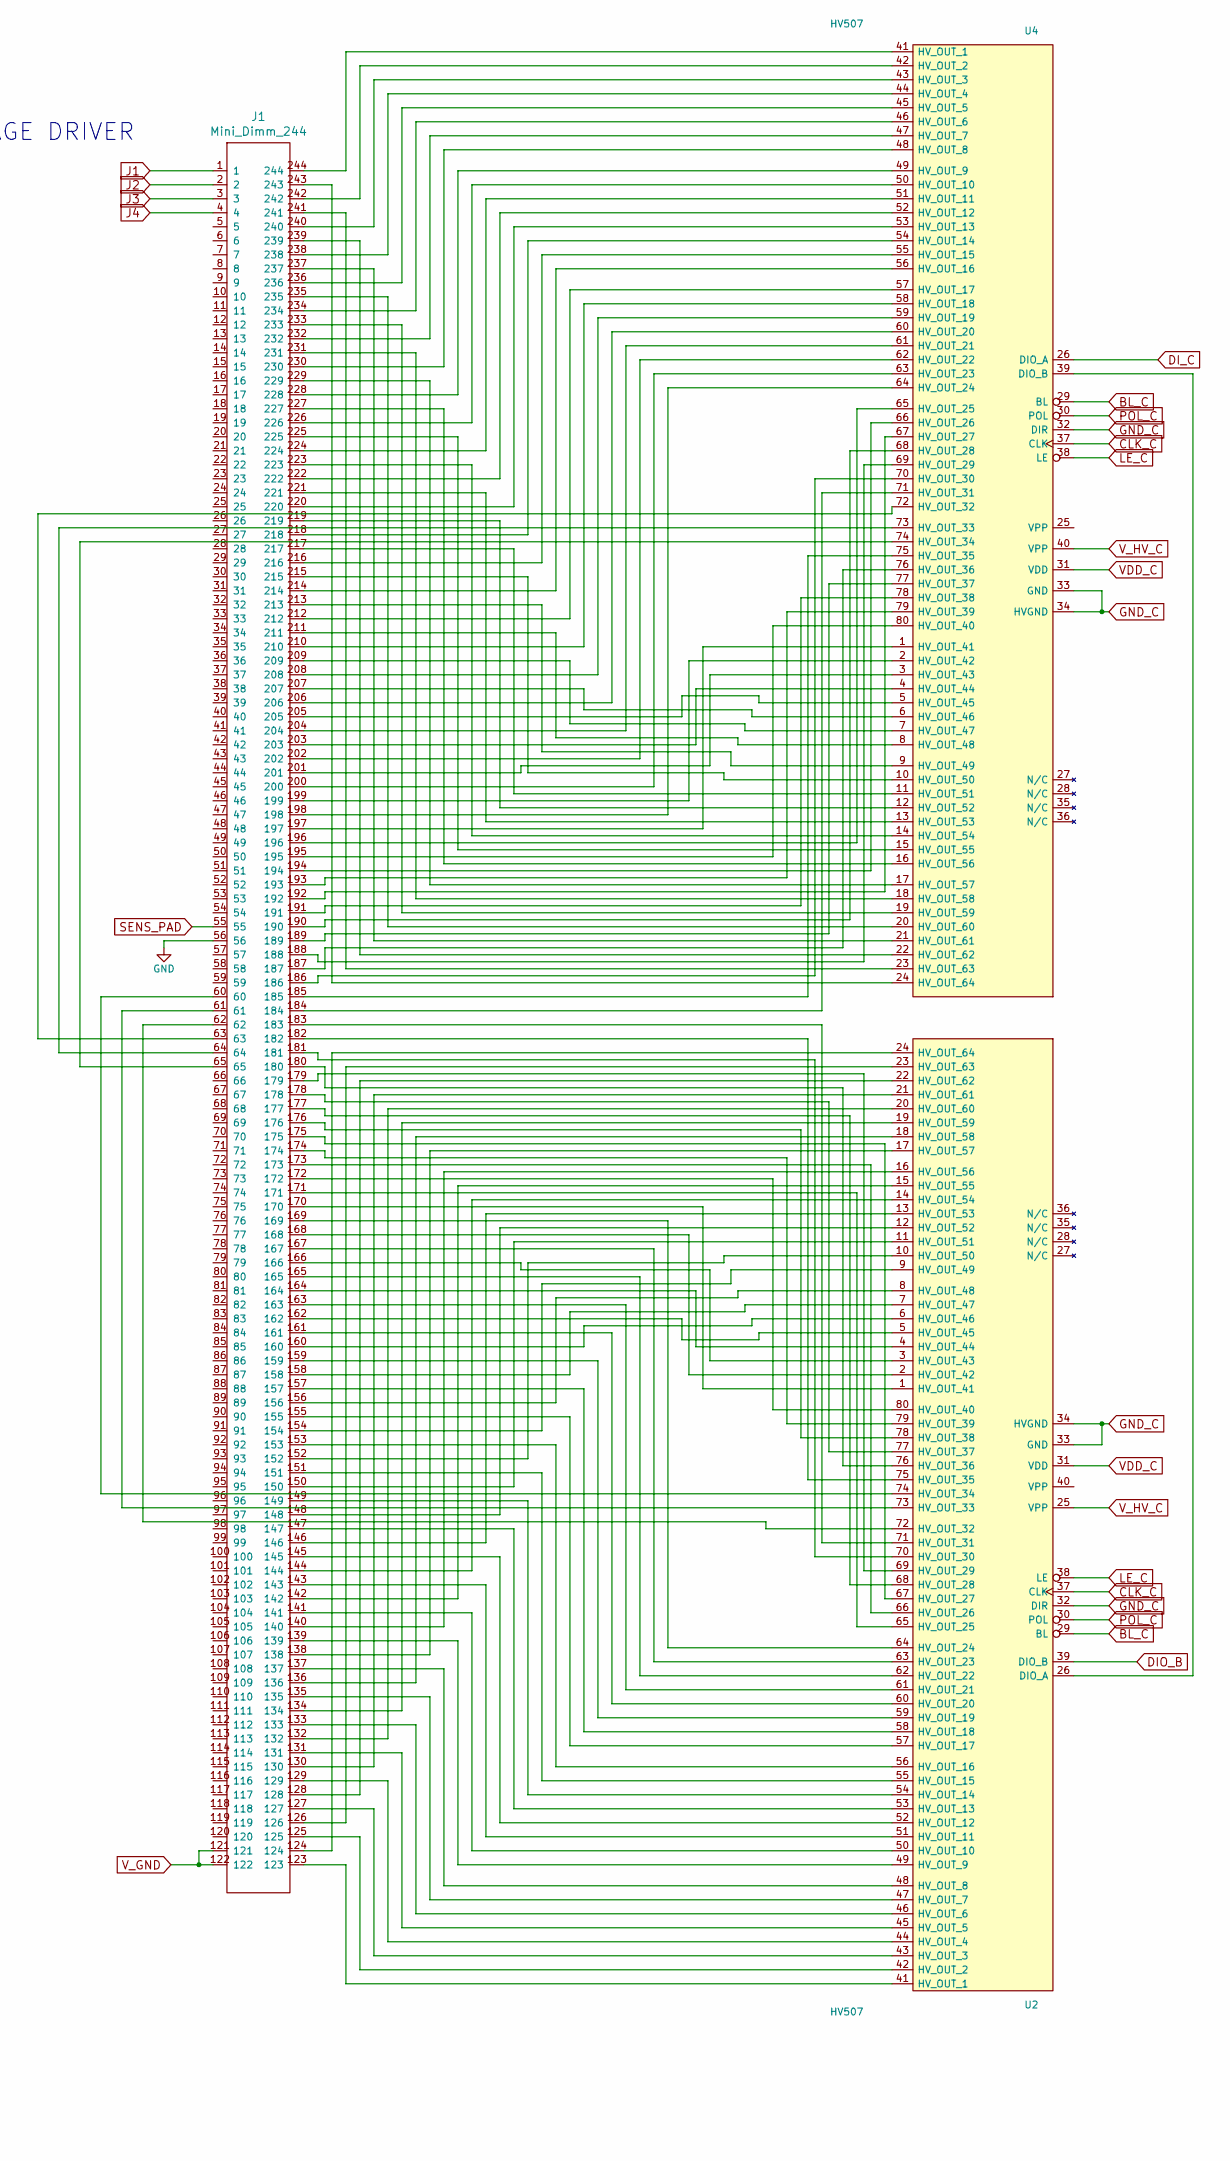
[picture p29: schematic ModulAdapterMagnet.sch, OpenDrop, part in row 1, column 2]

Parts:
+3V3: ScrewPad2; Measurement_Point_Square-SMD-Pad_Small
C1, C4, C12, C13: 100nF; C_0603_1608Metric
C2: 10uF; C_0603_1608Metric
C3, C5: 22nF; C_0603_1608Metric
GND1: ScrewPad2; Measurement_Point_Square-SMD-Pad_Small
J1: Mini_Dimm_244; MiniDimm_06_244_200
J2: Conn_01x24_Female; FFC_MOLEX_EASYON_05mm_24
J3, J4: Conn_02x02_Top_Bottom; PinHeader_2x02_P2.00mm_Vertical
M1: Motor_DC; GreaMotor6mm_Magnet_l
M2: Motor_DC; GreaMotor6mm_Magnet
P3: ScrewPad2; Measurement_Point_Square-SMD-Pad_Small
P13, P17: ScrewPad1; MountingHoleM3
P14, P15: ScrewPad2; MountingHoleM3
R1: 100k; R_0603_1608Metric
R2: 47k; R_0603_1608Metric
R3, R7: 4.7k; R_0603_1608Metric
R4, R5, R6, R8: 10k; R_0603_1608Metric
U1: TC78H660FTG; P-VQFN16-0303-0.50-001
U2, U4: HV507; PQFP-80_14x20mm_Pitch0.8mm
U3: MCP23008_SS; SSOP-20_5.3x7.2mm_P0.65mm
X1, X2, X3, X4, X5, X6: PAD; Fiducial_1mm_Dia_2.54mm_Outer_CopperBottom

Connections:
+3V3: +3V3.1, C1.1, C2.1, J2.1, J3.3, R1.1, R4.1, R5.1, R8.1, U1.3 (VM), U3.20 (VDD)
BL_C: J2.6, U2.29 (BL), U4.29 (BL)
BOOST: R7.2, U3.17 (GP5)
CLK_C: J2.12, U2.37 (CLK), U4.37 (CLK)
DIG0: J2.15, J3.1, R5.2, U3.1 (SCL)
DIG1: J2.14, J3.2, R4.2, U3.2 (SDA)
DI_C: J2.4, U4.26 (DIO_A)
ENABLE_A: U1.15 (IN1B/Enable_A), U3.12 (GP0)
ENABLE_B: U1.16 (IN2B/Enable_B), U3.14 (GP2)
GND: C1.2, C2.2, C3.2, C4.2, C5.2, GND1.1, J1.56, J2.3, J2.5, J2.7, J2.9, J2.11, J2.13, J2.17, J2.19, J2.21, J2.24, J3.4, R2.2, R3.2, U1.2 (AGND), U1.4 (PGND_A), U1.9 (PGND_B), U1.17 (GND_Pad), U3.3 (A2), U3.4 (A1), U3.5 (A0), U3.9 (VSS)
GND_C: C12.2, C13.2, J2.22, J2.23, U2.32 (DIR), U2.33 (GND), U2.34 (HVGND), U4.32 (DIR), U4.33 (GND), U4.34 (HVGND)
J1: J1.1, J4.1
J2: J1.2, J4.2
J3: J1.3, J4.3
J4: J1.4, J4.4
LE_C: J2.10, U2.38 (LE), U4.38 (LE)
MODE: R6.2, U3.16 (GP4)
unnamed: C3.1, R6.1, U1.13 (MODE/ERR)
unnamed: C4.1, R1.2, R3.1, R7.1, U1.10 (VREF)
unnamed: C5.1, R8.2, U3.6 (~RESET~)
unnamed: J1.60, U2.74 (HV_OUT_34)
unnamed: J1.61, U2.73 (HV_OUT_33)
unnamed: J1.62, U2.72 (HV_OUT_32)
unnamed: J1.63, U4.72 (HV_OUT_32)
unnamed: J1.64, U4.73 (HV_OUT_33)
unnamed: J1.65, U4.74 (HV_OUT_34)
unnamed: J1.123, U2.41 (HV_OUT_1)
unnamed: J1.124, U2.24 (HV_OUT_64)
unnamed: J1.125, U2.42 (HV_OUT_2)
unnamed: J1.126, U2.23 (HV_OUT_63)
unnamed: J1.127, U2.43 (HV_OUT_3)
unnamed: J1.128, U2.22 (HV_OUT_62)
unnamed: J1.129, U2.44 (HV_OUT_4)
unnamed: J1.130, U2.21 (HV_OUT_61)
unnamed: J1.131, U2.45 (HV_OUT_5)
unnamed: J1.132, U2.20 (HV_OUT_60)
unnamed: J1.133, U2.46 (HV_OUT_6)
unnamed: J1.134, U2.19 (HV_OUT_59)
unnamed: J1.135, U2.47 (HV_OUT_7)
unnamed: J1.136, U2.18 (HV_OUT_58)
unnamed: J1.137, U2.48 (HV_OUT_8)
unnamed: J1.138, U2.17 (HV_OUT_57)
unnamed: J1.139, U2.49 (HV_OUT_9)
unnamed: J1.140, U2.16 (HV_OUT_56)
unnamed: J1.141, U2.50 (HV_OUT_10)
unnamed: J1.142, U2.15 (HV_OUT_55)
unnamed: J1.143, U2.51 (HV_OUT_11)
unnamed: J1.144, U2.14 (HV_OUT_54)
unnamed: J1.145, U2.52 (HV_OUT_12)
unnamed: J1.146, U2.13 (HV_OUT_53)
unnamed: J1.147, U2.53 (HV_OUT_13)
unnamed: J1.148, U2.12 (HV_OUT_52)
unnamed: J1.149, U2.54 (HV_OUT_14)
unnamed: J1.150, U2.11 (HV_OUT_51)
unnamed: J1.151, U2.55 (HV_OUT_15)
unnamed: J1.152, U2.10 (HV_OUT_50)
unnamed: J1.153, U2.56 (HV_OUT_16)
unnamed: J1.154, U2.9 (HV_OUT_49)
unnamed: J1.155, U2.57 (HV_OUT_17)
unnamed: J1.156, U2.8 (HV_OUT_48)
unnamed: J1.157, U2.58 (HV_OUT_18)
unnamed: J1.158, U2.7 (HV_OUT_47)
unnamed: J1.159, U2.59 (HV_OUT_19)
unnamed: J1.160, U2.6 (HV_OUT_46)
unnamed: J1.161, U2.60 (HV_OUT_20)
unnamed: J1.162, U2.5 (HV_OUT_45)
unnamed: J1.163, U2.61 (HV_OUT_21)
unnamed: J1.164, U2.4 (HV_OUT_44)
unnamed: J1.165, U2.62 (HV_OUT_22)
unnamed: J1.166, U2.3 (HV_OUT_43)
unnamed: J1.167, U2.63 (HV_OUT_23)
unnamed: J1.168, U2.2 (HV_OUT_42)
unnamed: J1.169, U2.64 (HV_OUT_24)
unnamed: J1.170, U2.1 (HV_OUT_41)
unnamed: J1.171, U2.65 (HV_OUT_25)
unnamed: J1.172, U2.80 (HV_OUT_40)
unnamed: J1.173, U2.66 (HV_OUT_26)
unnamed: J1.174, U2.79 (HV_OUT_39)
unnamed: J1.175, U2.67 (HV_OUT_27)
unnamed: J1.176, U2.78 (HV_OUT_38)
unnamed: J1.177, U2.68 (HV_OUT_28)
unnamed: J1.178, U2.77 (HV_OUT_37)
unnamed: J1.179, U2.69 (HV_OUT_29)
unnamed: J1.180, U2.76 (HV_OUT_36)
unnamed: J1.181, U2.70 (HV_OUT_30)
unnamed: J1.182, U2.75 (HV_OUT_35)
unnamed: J1.183, U2.71 (HV_OUT_31)
unnamed: J1.184, U4.71 (HV_OUT_31)
unnamed: J1.185, U4.75 (HV_OUT_35)
unnamed: J1.186, U4.70 (HV_OUT_30)
unnamed: J1.187, U4.76 (HV_OUT_36)
unnamed: J1.188, U4.69 (HV_OUT_29)
unnamed: J1.189, U4.77 (HV_OUT_37)
unnamed: J1.190, U4.68 (HV_OUT_28)
unnamed: J1.191, U4.78 (HV_OUT_38)
unnamed: J1.192, U4.67 (HV_OUT_27)
unnamed: J1.193, U4.79 (HV_OUT_39)
unnamed: J1.194, U4.66 (HV_OUT_26)
unnamed: J1.195, U4.80 (HV_OUT_40)
unnamed: J1.196, U4.65 (HV_OUT_25)
unnamed: J1.197, U4.1 (HV_OUT_41)
unnamed: J1.198, U4.64 (HV_OUT_24)
unnamed: J1.199, U4.2 (HV_OUT_42)
unnamed: J1.200, U4.63 (HV_OUT_23)
unnamed: J1.201, U4.3 (HV_OUT_43)
unnamed: J1.202, U4.62 (HV_OUT_22)
unnamed: J1.203, U4.4 (HV_OUT_44)
unnamed: J1.204, U4.61 (HV_OUT_21)
unnamed: J1.205, U4.5 (HV_OUT_45)
unnamed: J1.206, U4.60 (HV_OUT_20)
unnamed: J1.207, U4.6 (HV_OUT_46)
unnamed: J1.208, U4.59 (HV_OUT_19)
unnamed: J1.209, U4.7 (HV_OUT_47)
unnamed: J1.210, U4.58 (HV_OUT_18)
unnamed: J1.211, U4.8 (HV_OUT_48)
unnamed: J1.212, U4.57 (HV_OUT_17)
unnamed: J1.213, U4.9 (HV_OUT_49)
unnamed: J1.214, U4.56 (HV_OUT_16)
unnamed: J1.215, U4.10 (HV_OUT_50)
unnamed: J1.216, U4.55 (HV_OUT_15)
unnamed: J1.217, U4.11 (HV_OUT_51)
unnamed: J1.218, U4.54 (HV_OUT_14)
unnamed: J1.219, U4.12 (HV_OUT_52)
unnamed: J1.220, U4.53 (HV_OUT_13)
unnamed: J1.221, U4.13 (HV_OUT_53)
unnamed: J1.222, U4.52 (HV_OUT_12)
unnamed: J1.223, U4.14 (HV_OUT_54)
unnamed: J1.224, U4.51 (HV_OUT_11)
unnamed: J1.225, U4.15 (HV_OUT_55)
unnamed: J1.226, U4.50 (HV_OUT_10)
unnamed: J1.227, U4.16 (HV_OUT_56)
unnamed: J1.228, U4.49 (HV_OUT_9)
unnamed: J1.229, U4.17 (HV_OUT_57)
unnamed: J1.230, U4.48 (HV_OUT_8)
unnamed: J1.231, U4.18 (HV_OUT_58)
unnamed: J1.232, U4.47 (HV_OUT_7)
unnamed: J1.233, U4.19 (HV_OUT_59)
unnamed: J1.234, U4.46 (HV_OUT_6)
unnamed: J1.235, U4.20 (HV_OUT_60)
unnamed: J1.236, U4.45 (HV_OUT_5)
unnamed: J1.237, U4.21 (HV_OUT_61)
unnamed: J1.238, U4.44 (HV_OUT_4)
unnamed: J1.239, U4.22 (HV_OUT_62)
unnamed: J1.240, U4.43 (HV_OUT_3)
unnamed: J1.241, U4.23 (HV_OUT_63)
unnamed: J1.242, U4.42 (HV_OUT_2)
unnamed: J1.243, U4.24 (HV_OUT_64)
unnamed: J1.244, U4.41 (HV_OUT_1)
unnamed: M1.1 (+), U1.5 (OUT_A+)
unnamed: M1.2 (-), U1.6 (OUT_A-)
unnamed: M2.1 (+), U1.8 (OUT_B+)
unnamed: M2.2 (-), U1.7 (OUT_B-)
unnamed: P3.1, U3.19 (GP7)
unnamed: R2.1, U1.11 (OSCM)
unnamed: U2.26 (DIO_A), U4.39 (DIO_B)
PHASE_A: U1.1 (IN1A/Phase_A), U3.13 (GP1)
PHASE_B: U1.14 (IN2A/Phase_B), U3.15 (GP3)
POL_C: J2.8, U2.30 (POL), U4.30 (POL)
SENS_PAD: J1.55, J2.16
STBY: U1.12 (STBY), U3.18 (GP6)
VDD_C: C12.1, C13.1, J2.18, U2.31 (VDD), U4.31 (VDD)
V_GND: J1.121, J1.122, J2.2
V_HV_C: J2.20, U2.25 (VPP), U4.40 (VPP)

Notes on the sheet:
HIGH VOLTAGE DRIVER
FLUXL_X_Y
78mV/1100mV * 2A = 138mA 147mV/1100mV * 2A = 267mA 1130V/1100mV *2A = 2A

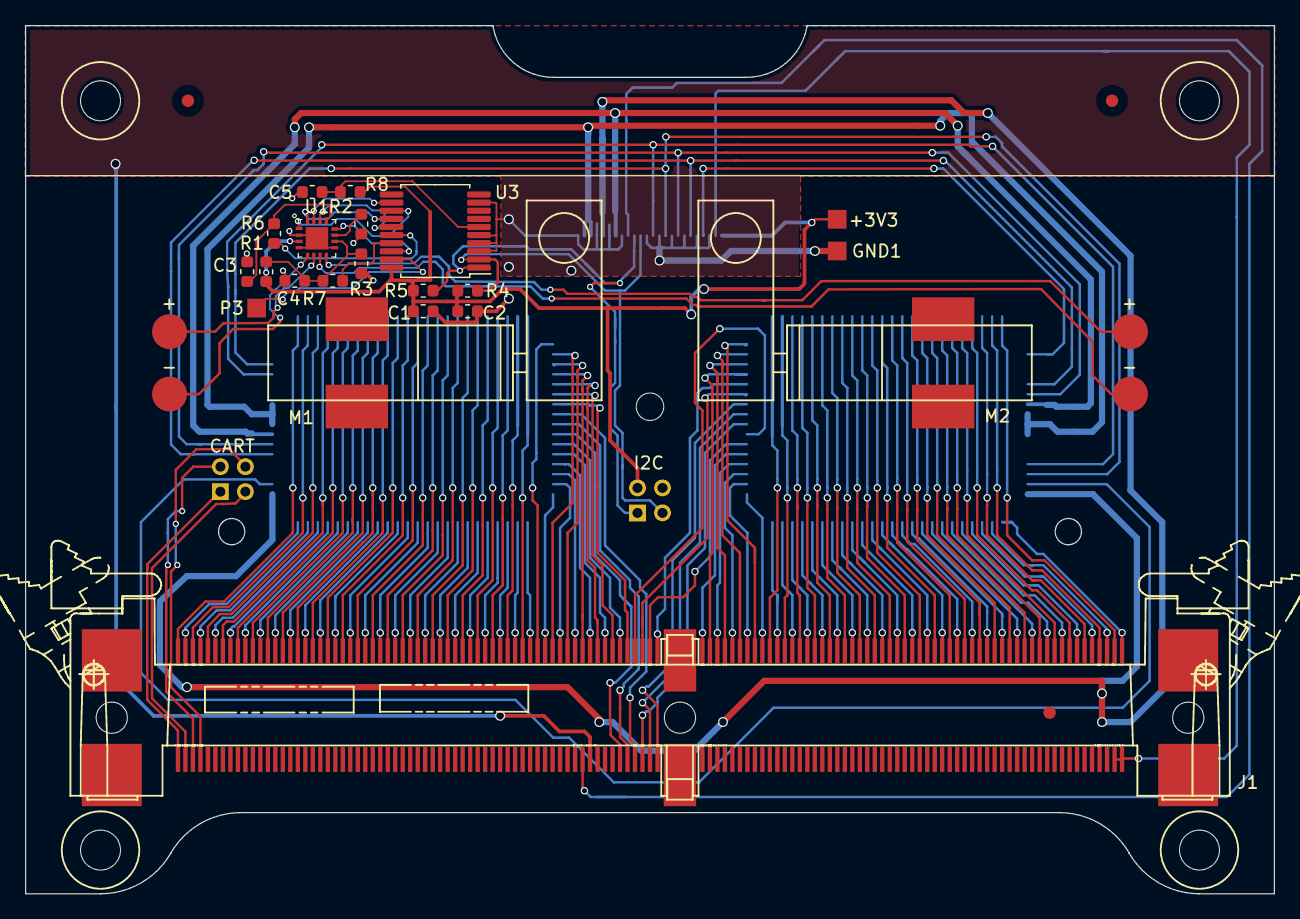
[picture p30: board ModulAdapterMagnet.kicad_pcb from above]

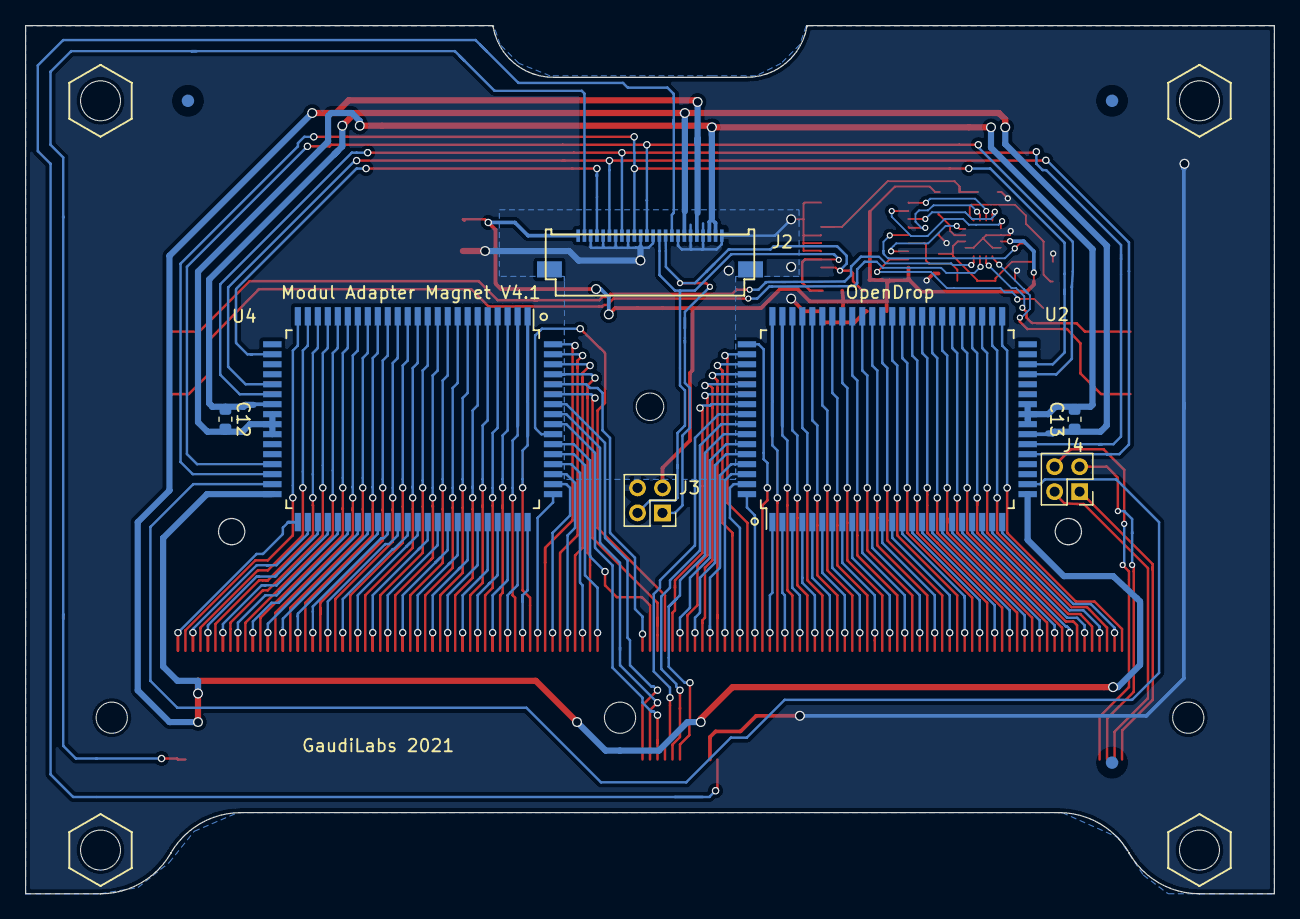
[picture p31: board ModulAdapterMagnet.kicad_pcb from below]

Board: 2 copper layers, 100.0 x 69.5 mm, 38 parts (10 on the bottom side), 163 nets.

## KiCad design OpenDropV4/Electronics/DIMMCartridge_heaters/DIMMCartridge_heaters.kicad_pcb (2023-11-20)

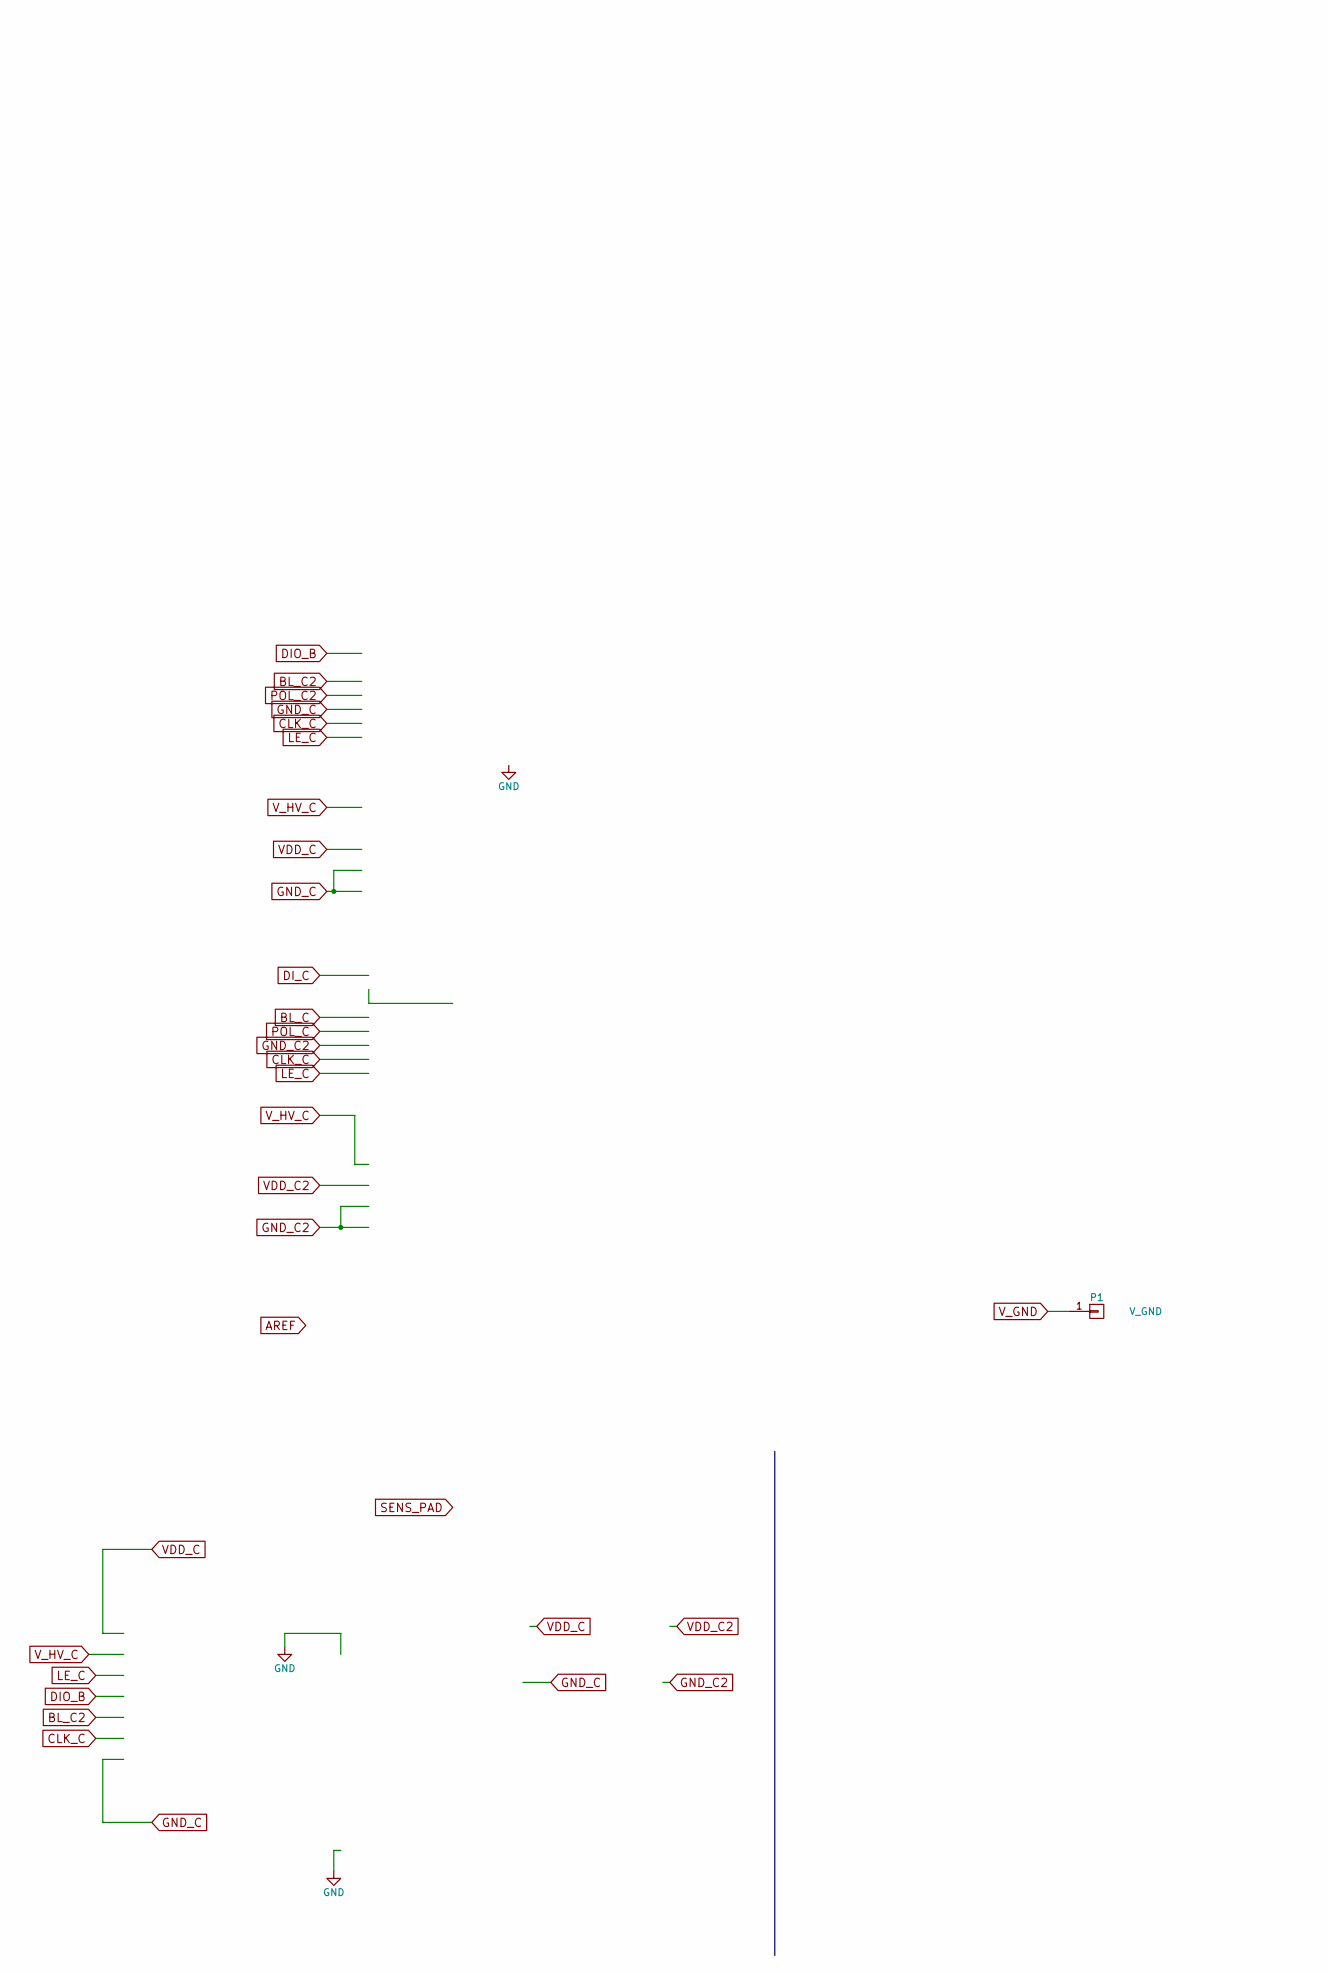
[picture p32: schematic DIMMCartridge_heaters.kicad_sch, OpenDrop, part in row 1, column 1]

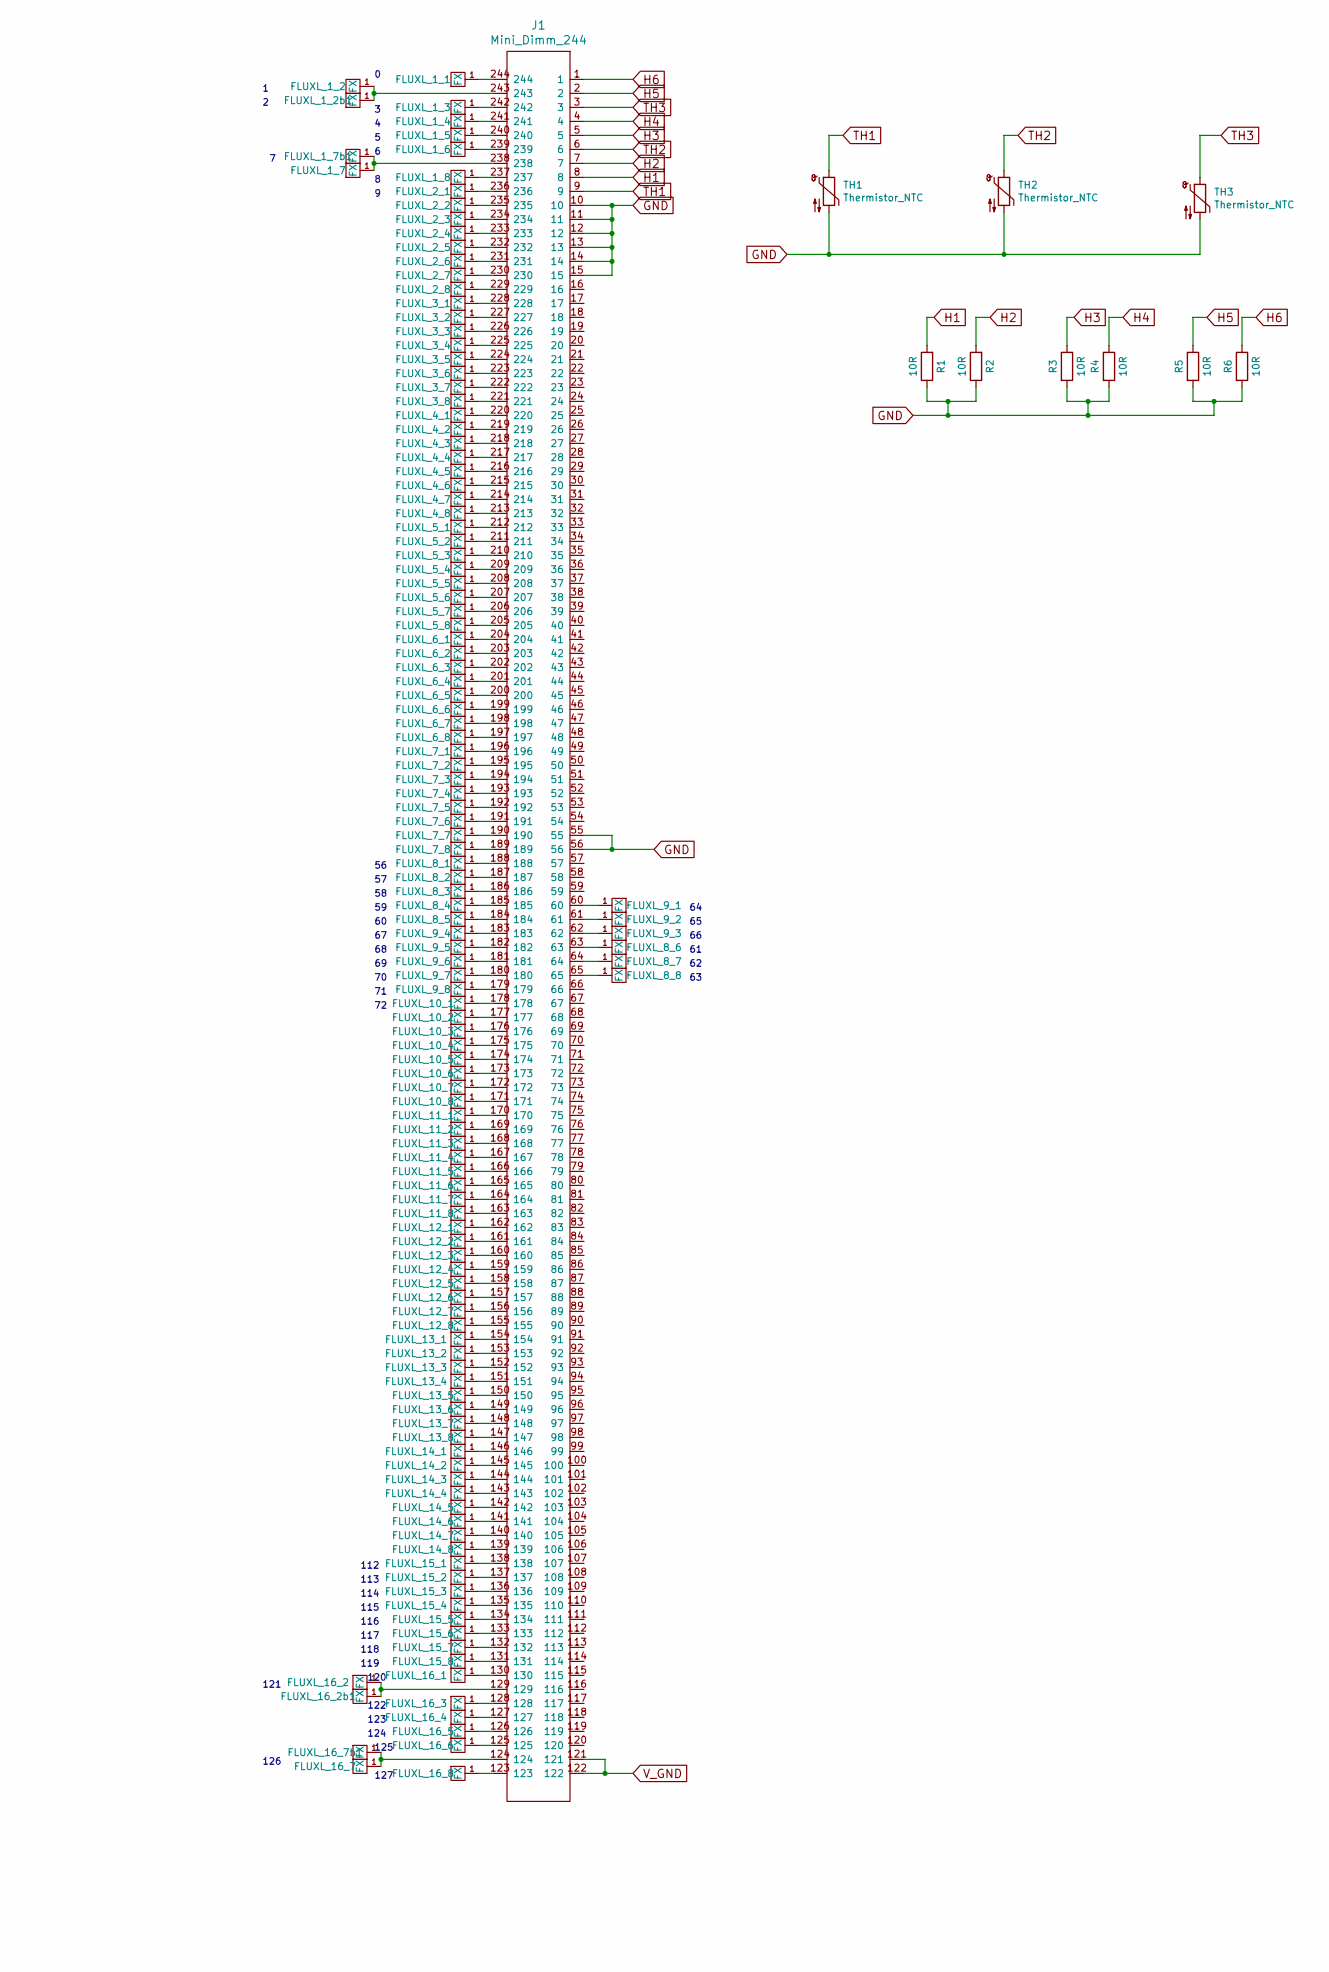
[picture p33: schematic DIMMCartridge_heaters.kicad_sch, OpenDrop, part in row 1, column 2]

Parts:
FLUXL_1_1, FLUXL_1_8, FLUXL_16_1, FLUXL_16_8: FX; FLUXPAD_2_75_4MIL_4_5_res1
FLUXL_1_2, FLUXL_1_7, FLUXL_16_2, FLUXL_16_7: FX; FLUXPAD_2_75_4MIL_4_5_res4
FLUXL_1_2b1, FLUXL_1_7b1, FLUXL_16_2b1, FLUXL_16_7b1: FX; FLUXPAD_2_75_4MIL_4_5_res5
FLUXL_1_3, FLUXL_1_6, FLUXL_16_3, FLUXL_16_6: FX; FLUXPAD_2_75_4MIL_4_5_res2
FLUXL_1_4, FLUXL_1_5, FLUXL_16_4, FLUXL_16_5: FX; FLUXPAD_2_75_4MIL_4_5_res3
FLUXL_2_1, FLUXL_15_8: FX; FLUXPAD_2_75_4MIL_4_5_topleft
FLUXL_2_2, FLUXL_2_7, FLUXL_3_2, FLUXL_3_3, FLUXL_3_4, FLUXL_3_5, FLUXL_3_6, FLUXL_3_7, FLUXL_4_4, FLUXL_4_5, FLUXL_4_6, FLUXL_4_7, FLUXL_5_2, FLUXL_5_3, FLUXL_5_4, FLUXL_5_5, FLUXL_5_6, FLUXL_5_7, FLUXL_6_2, FLUXL_6_3, FLUXL_6_4, FLUXL_6_5, FLUXL_6_6, FLUXL_6_7, FLUXL_7_2, FLUXL_7_3, FLUXL_7_4, FLUXL_7_5, FLUXL_7_6, FLUXL_7_7, FLUXL_8_4, FLUXL_8_5, FLUXL_8_6, FLUXL_8_7, FLUXL_9_2, FLUXL_9_3, FLUXL_9_4, FLUXL_9_5, FLUXL_9_6, FLUXL_9_7, FLUXL_10_2, FLUXL_10_3, FLUXL_10_4, FLUXL_10_5, FLUXL_10_6, FLUXL_10_7, FLUXL_11_2, FLUXL_11_3, FLUXL_11_4, FLUXL_11_5, FLUXL_11_6, FLUXL_11_7, FLUXL_12_2, FLUXL_12_3, FLUXL_12_4, FLUXL_12_5, FLUXL_12_6, FLUXL_12_7, FLUXL_13_4, FLUXL_13_5, FLUXL_13_6, FLUXL_13_7, FLUXL_14_2, FLUXL_14_3, FLUXL_14_4, FLUXL_14_5, FLUXL_14_6, FLUXL_14_7, FLUXL_15_2, FLUXL_15_7: FX; FLUXPAD_2_75_4MIL_4_6
FLUXL_2_3, FLUXL_2_4, FLUXL_2_5, FLUXL_2_6, FLUXL_15_3, FLUXL_15_4, FLUXL_15_5, FLUXL_15_6: FX; FLUXPAD_2_75_4MIL_4_5_side
FLUXL_2_8, FLUXL_15_1: FX; FLUXPAD_2_75_4MIL_4_5_topright
FLUXL_3_1, FLUXL_3_8, FLUXL_4_1, FLUXL_4_8, FLUXL_5_1, FLUXL_5_8, FLUXL_6_1, FLUXL_6_8, FLUXL_7_1, FLUXL_7_8, FLUXL_8_1, FLUXL_8_8, FLUXL_9_1, FLUXL_9_8, FLUXL_10_1, FLUXL_10_8, FLUXL_11_1, FLUXL_11_8, FLUXL_12_1, FLUXL_12_8, FLUXL_13_1, FLUXL_13_8, FLUXL_14_1, FLUXL_14_8: FX; FLUXPAD_2_75_4MIL_4_6_top
FLUXL_4_2, FLUXL_4_3, FLUXL_8_2, FLUXL_8_3, FLUXL_13_2, FLUXL_13_3: FX; FLUXPAD_2_75_4MIL_4_5_TempSens
J1: Mini_Dimm_244; Mini_Dimm_Cartridge_244_ok
P1: V_GND; Pad_4mm_10mm
R1, R2, R3, R4, R5, R6: 10R; R_1206_3216Metric_heater
TH1, TH2, TH3: Thermistor_NTC; R_0402_1005Metric_TempSens

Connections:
GND: J1.10, J1.11, J1.12, J1.13, J1.14, J1.15, J1.55, J1.56, R1.1, R2.1, R3.2, R4.2, R5.2, R6.2, TH1.2, TH2.2, TH3.2
H1: J1.8, R1.2
H2: J1.7, R2.2
H3: J1.5, R3.1
H4: J1.4, R4.1
H5: J1.2, R5.1
H6: J1.1, R6.1
unnamed: FLUXL_1_1.1, J1.244
unnamed: FLUXL_1_2.1, FLUXL_1_2b1.1, J1.243
unnamed: FLUXL_1_3.1, J1.242
unnamed: FLUXL_1_4.1, J1.241
unnamed: FLUXL_1_5.1, J1.240
unnamed: FLUXL_1_6.1, J1.239
unnamed: FLUXL_1_7.1, FLUXL_1_7b1.1, J1.238
unnamed: FLUXL_1_8.1, J1.237
unnamed: FLUXL_2_1.1, J1.236
unnamed: FLUXL_2_2.1, J1.235
unnamed: FLUXL_2_3.1, J1.234
unnamed: FLUXL_2_4.1, J1.233
unnamed: FLUXL_2_5.1, J1.232
unnamed: FLUXL_2_6.1, J1.231
unnamed: FLUXL_2_7.1, J1.230
unnamed: FLUXL_2_8.1, J1.229
unnamed: FLUXL_3_1.1, J1.228
unnamed: FLUXL_3_2.1, J1.227
unnamed: FLUXL_3_3.1, J1.226
unnamed: FLUXL_3_4.1, J1.225
unnamed: FLUXL_3_5.1, J1.224
unnamed: FLUXL_3_6.1, J1.223
unnamed: FLUXL_3_7.1, J1.222
unnamed: FLUXL_3_8.1, J1.221
unnamed: FLUXL_4_1.1, J1.220
unnamed: FLUXL_4_2.1, J1.219
unnamed: FLUXL_4_3.1, J1.218
unnamed: FLUXL_4_4.1, J1.217
unnamed: FLUXL_4_5.1, J1.216
unnamed: FLUXL_4_6.1, J1.215
unnamed: FLUXL_4_7.1, J1.214
unnamed: FLUXL_4_8.1, J1.213
unnamed: FLUXL_5_1.1, J1.212
unnamed: FLUXL_5_2.1, J1.211
unnamed: FLUXL_5_3.1, J1.210
unnamed: FLUXL_5_4.1, J1.209
unnamed: FLUXL_5_5.1, J1.208
unnamed: FLUXL_5_6.1, J1.207
unnamed: FLUXL_5_7.1, J1.206
unnamed: FLUXL_5_8.1, J1.205
unnamed: FLUXL_6_1.1, J1.204
unnamed: FLUXL_6_2.1, J1.203
unnamed: FLUXL_6_3.1, J1.202
unnamed: FLUXL_6_4.1, J1.201
unnamed: FLUXL_6_5.1, J1.200
unnamed: FLUXL_6_6.1, J1.199
unnamed: FLUXL_6_7.1, J1.198
unnamed: FLUXL_6_8.1, J1.197
unnamed: FLUXL_7_1.1, J1.196
unnamed: FLUXL_7_2.1, J1.195
unnamed: FLUXL_7_3.1, J1.194
unnamed: FLUXL_7_4.1, J1.193
unnamed: FLUXL_7_5.1, J1.192
unnamed: FLUXL_7_6.1, J1.191
unnamed: FLUXL_7_7.1, J1.190
unnamed: FLUXL_7_8.1, J1.189
unnamed: FLUXL_8_1.1, J1.188
unnamed: FLUXL_8_2.1, J1.187
unnamed: FLUXL_8_3.1, J1.186
unnamed: FLUXL_8_4.1, J1.185
unnamed: FLUXL_8_5.1, J1.184
unnamed: FLUXL_8_6.1, J1.63
unnamed: FLUXL_8_7.1, J1.64
unnamed: FLUXL_8_8.1, J1.65
unnamed: FLUXL_9_1.1, J1.60
unnamed: FLUXL_9_2.1, J1.61
unnamed: FLUXL_9_3.1, J1.62
unnamed: FLUXL_9_4.1, J1.183
unnamed: FLUXL_9_5.1, J1.182
unnamed: FLUXL_9_6.1, J1.181
unnamed: FLUXL_9_7.1, J1.180
unnamed: FLUXL_9_8.1, J1.179
unnamed: FLUXL_10_1.1, J1.178
unnamed: FLUXL_10_2.1, J1.177
unnamed: FLUXL_10_3.1, J1.176
unnamed: FLUXL_10_4.1, J1.175
unnamed: FLUXL_10_5.1, J1.174
unnamed: FLUXL_10_6.1, J1.173
unnamed: FLUXL_10_7.1, J1.172
unnamed: FLUXL_10_8.1, J1.171
unnamed: FLUXL_11_1.1, J1.170
unnamed: FLUXL_11_2.1, J1.169
unnamed: FLUXL_11_3.1, J1.168
unnamed: FLUXL_11_4.1, J1.167
unnamed: FLUXL_11_5.1, J1.166
unnamed: FLUXL_11_6.1, J1.165
unnamed: FLUXL_11_7.1, J1.164
unnamed: FLUXL_11_8.1, J1.163
unnamed: FLUXL_12_1.1, J1.162
unnamed: FLUXL_12_2.1, J1.161
unnamed: FLUXL_12_3.1, J1.160
unnamed: FLUXL_12_4.1, J1.159
unnamed: FLUXL_12_5.1, J1.158
unnamed: FLUXL_12_6.1, J1.157
unnamed: FLUXL_12_7.1, J1.156
unnamed: FLUXL_12_8.1, J1.155
unnamed: FLUXL_13_1.1, J1.154
unnamed: FLUXL_13_2.1, J1.153
unnamed: FLUXL_13_3.1, J1.152
unnamed: FLUXL_13_4.1, J1.151
unnamed: FLUXL_13_5.1, J1.150
unnamed: FLUXL_13_6.1, J1.149
unnamed: FLUXL_13_7.1, J1.148
unnamed: FLUXL_13_8.1, J1.147
unnamed: FLUXL_14_1.1, J1.146
unnamed: FLUXL_14_2.1, J1.145
unnamed: FLUXL_14_3.1, J1.144
unnamed: FLUXL_14_4.1, J1.143
unnamed: FLUXL_14_5.1, J1.142
unnamed: FLUXL_14_6.1, J1.141
unnamed: FLUXL_14_7.1, J1.140
unnamed: FLUXL_14_8.1, J1.139
unnamed: FLUXL_15_1.1, J1.138
unnamed: FLUXL_15_2.1, J1.137
unnamed: FLUXL_15_3.1, J1.136
unnamed: FLUXL_15_4.1, J1.135
unnamed: FLUXL_15_5.1, J1.134
unnamed: FLUXL_15_6.1, J1.133
unnamed: FLUXL_15_7.1, J1.132
unnamed: FLUXL_15_8.1, J1.131
unnamed: FLUXL_16_1.1, J1.130
unnamed: FLUXL_16_2.1, FLUXL_16_2b1.1, J1.129
unnamed: FLUXL_16_3.1, J1.128
unnamed: FLUXL_16_4.1, J1.127
unnamed: FLUXL_16_5.1, J1.126
unnamed: FLUXL_16_6.1, J1.125
unnamed: FLUXL_16_7.1, FLUXL_16_7b1.1, J1.124
unnamed: FLUXL_16_8.1, J1.123
TH1: J1.9, TH1.1
TH2: J1.6, TH2.1
TH3: J1.3, TH3.1
V_GND: J1.121, J1.122, P1.1

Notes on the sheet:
120
122
118
117
121
126
124
115
123
127
114
116
112
119
113
125

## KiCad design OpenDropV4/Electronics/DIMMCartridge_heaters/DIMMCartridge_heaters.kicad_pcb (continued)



Board: 2 copper layers, 82.0 x 54.5 mm, 143 parts (9 on the bottom side), 139 nets.

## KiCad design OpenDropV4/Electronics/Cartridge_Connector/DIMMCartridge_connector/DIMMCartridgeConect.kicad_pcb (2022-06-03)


Board: 2 copper layers, 82.0 x 54.5 mm, 4 parts (0 on the bottom side), 36 nets.

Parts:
J1: Mini_Dimm_244; Mini_Dimm_Cartridge_06_244
J2, J3: Conn_02x17_Odd_Even; IDC-Header_2x17_P2.54mm_Vertical_Lock
P1: V_GND; Pad_4mm_10mm

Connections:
1_1: J1.244, J3.11
1_2: J1.243, J3.9
2_1: J1.236, J3.13
2_2: J1.235, J3.7
3_1: J1.228, J3.15
3_2: J1.227, J3.5
4_1: J1.220, J3.17
4_2: J1.219, J3.3
5_1: J1.212, J3.19
5_2: J1.211, J3.33
6_1: J1.204, J3.21
6_2: J1.203, J3.31
7_1: J1.196, J3.23
7_2: J1.195, J3.29
8_1: J1.188, J3.25
8_2: J1.187, J3.27
9_1: J1.60, J2.9
9_2: J1.61, J2.7
10_1: J1.178, J2.11
10_2: J1.177, J2.5
11_1: J1.170, J2.13
11_2: J1.169, J2.3
12_1: J1.162, J2.15
12_2: J1.161, J2.1
13_1: J1.154, J2.17
13_2: J1.153, J2.31
14_1: J1.146, J2.19
14_2: J1.145, J2.29
15_1: J1.138, J2.21
15_2: J1.137, J2.27
16_1: J1.130, J2.23
16_2: J1.129, J2.25
DETECT1: J1.55, J3.2
DETECT2: J1.56, J2.4
unnamed: J2.2, J3.4
V_GND: J1.121, J1.122, J2.33, J3.1, P1.1

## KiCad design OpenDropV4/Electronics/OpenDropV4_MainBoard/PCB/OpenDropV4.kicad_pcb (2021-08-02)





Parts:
C1, C19: 100uF, 6.3V; C_1206_3216Metric
C2, C3, C13, C14, C22, C26, C30, C31, C33, C34, C36: 100nF; C_0805
C4, C18: 4u7, 250V; C_Elec_8x10.2
C5, C21: 100uF, 6.3V; C_1206
C6, C35: 100nF, 250V; C_1812_4532Metric_Pad1.30x3.40mm_HandSolder
C7, C9, C11, C15, C16, C20, C24, C27: 1uF; C_0805
C8, C10: 2.2uF; C_0805
C17: 1pF; C_0805
C23, C25: 22pF; C_0805
C28, C29: 3.3nF; C_0805
C37: 470pF; C_0805
D1: ES2F; DO-214AA
D2, D3: 1N4148; D_SOD-323
D4: PESD5V0L5UY; SOT-363_SC-70-6
D5: D_TVS; DO-214AA
FB1, FB2, FB3, FB4, FB5, FB6, FB8: Ferrite_Bead_Small; L_0603_1608Metric
J1: USB_C_Receptacle; USB_C_Receptacle_Amphenol_12401610E4-2A
J2: Conn_02x05_Odd_Even; Pin_Header_Straight_2x05_Pitch1.27mm_SMD
J3: Conn_01x24_Female; FFC_MOLEX_EASYON_05mm_24
JS2: JoystickSMD_SKRH; SKRHABE010
L1: 100uH; SRN1060
LED1, LED2, LED3: LED; LED_0603_1608Metric
P1, P3, P7, P12: CONN_01X01; Measurement_Point_Square-SMD-Pad_Small
P2: ScrewPad4; Measurement_Point_Croki
P13: ScrewPad1; MountingHoleM3
P14: ScrewPad2; MountingHoleM3
P15: ScrewPad3; MountingHoleM3
P16: ScrewPad4; MountingHoleM3
R1: 6.8k; R_0805
R2: 1M5; R_2512
R3, R9: 390k; R_0805
R4, R6, R8, R13: 390; R_0805
R5, R10, R18, R19, R20, R21, R22, R30, R44: 10k; R_0805
R7: 6.8k; R_0805_2012Metric
R11, R31: 15k; R_0805
R12: 2.2k; R_0805
R14: 10k; R_0805_2012Metric
R29: 680k?; R_0805
R32, R34, R36, R37, R40, R41, R45, R48, R49, R51: 220; R_0805
R46, R47: 5k; R_0805
RSENSE1: 0R1; R_2010
S1: OLED_DISPLAY; OLED_096_1_Flip
SP1: SPEAKER; Speaker16mm
SW1, SW2: SW_PUSH; PUSH_BUTTON_SMD
SW3: SW_PUSH; SW_SPST_KMS221GLFS
SW5: SPST; Switch_On-On
T1: TK560P60Y; D-Pak_TO252AA
U1: MAX1771ESA; SO08
U3: PAM8301; SOT-23-6
U5: SAMD21G18B-A changed from SAML21; TQFP-48_7x7mm_Pitch0.5mm
U6: MCP6002; SO08
U7, U8, U9: ACPL-024L-000E; HCPL_Optocoupler_SMD
U10, U11, U12, U13: AQY210EH; SMD_DIP4
U14: TLV1117-33; SOT-223
U15: MCP41050; SO08
U16: 74xx14; SOIC-14_N
Y1: 32.765; Crystal_SMD_3215-2pin_3.2x1.5mm

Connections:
+3V3: C14.1, C15.1, C21.1, C22.2, C26.1, C30.1, C33.2, C34.2, J2.1, J3.1, R4.1, R5.2, R11.2, R18.2, R22.1, S1.6 (VBAT), S1.9 (VDD), U3.4 (~SD), U3.5 (VDD), U5.6 (VDDANA), U5.17 (VDDIO), U5.36 (VDDIO), U5.44 (VDDIN), U6.8 (V+), U14.2 (VO), U15.8 (VDD)
AC: C31.1, U5.7 (EXTINT8/AIN2/OAOUT1/SERCOM4PAD0/TC0WO0/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)
AREF: C24.2, U5.4 (Y1/AIN1/VREFA/VREFP/PA03)
BL: R40.2, U5.12 (EXTINT7EXTWAKE7/AIN7/AIN3/OAOUT0/SERCOM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)
BL_C: D4.6 (K5), FB4.1, J3.6
CLK: R32.2, U5.20 (EXTINT11/Y3/SERCOM4PAD3/TC1WO1/TCC0WO5/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)
CLK_C: D4.3 (K2), FB1.1, J3.12
D13: R8.1, U5.26 (EXTINT1/X5/SERCOM1PAD1/SERCOM3PAD1/TCC2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)
D+: J1.A6 (D+), J1.B6 (D+), U5.34 (EXTINT13/SERCOM3PAD3/SERCOM5PAD3/TC1WO1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)
D-: J1.A7 (D-), J1.B7 (D-), U5.33 (EXTINT12/SERCOM3PAD2/SERCOM5PAD2/TC1WO1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)
DI: R34.2, U5.19 (EXTINT10/Y2/SERCOM4PAD2/TC1WO0/TCC0WO4/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)
DIG0: J3.15, U5.14 (EXTINT9/AIN17/X1Y7/SERCOM0PAD1/SERCOM2P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)
DIG1: J3.14, U5.13 (NMI/AIN16/X0Y6/SERCOM0PAD0/SERCOM2PAD0/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)
DISP_CS: S1.13 (CS), U5.21 (ACCMP0/TC2WO0/SERCOM4P0/SERCOM2P0/PA12)
DISP_DC: S1.15 (D/C#_SA0), U5.16 (EXTINT11/AIN19/X3Y9/SERCOM0PAD3/SERCOM2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)
DISP_RES: S1.14 (RES), U5.24 (XOUT/EXTINT15/SERCOM2PAD3/SERCOM4PAD3/T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)
DISP_SCL: S1.18 (D0_(SCL)), U5.32 (EXTINT7/X11/SERCOM3PAD1/SERCOM5PAD1/TC0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)
DISP_SDA: S1.19 (D1_(SA)), U5.31 (EXTINT6/X10/SERCOM3PAD0/SERCOM5PAD0/TC0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)
DI_C: D4.4 (K3), FB5.1, J3.4
FEEDBACK: C17.1, R31.1, U5.8 (EXTINT9/AIN3/Y15/OAPOS1/SERCOM4PAD1/TC0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), U6.1
GND: C1.2, C2.2, C3.2, C4.2, C5.2, C6.2, C8.2, C10.2, C14.2, C15.2, C20.2, C21.2, C22.1, C23.1, C24.1, C25.1, C26.2, C27.1, C28.1, C29.1, C30.2, C33.1, C34.1, J1.A1 (GND), J1.A12 (GND), J1.B1 (GND), J1.B12 (GND), J2.3, J2.5, J2.9, J3.3, J3.5, J3.7, J3.9, J3.11, J3.13, J3.17, J3.19, J3.21, J3.24, JS2.5 (Common), LED1.1 (K), LED2.1 (K), LED3.1 (K), P2.1, P3.1, R1.2, R3.2, R13.2, R14.2, R29.1, R30.2, R46.2, R47.2, RSENSE1.2, S1.8 (VSS), S1.10 (BS0), S1.11 (BS1), S1.12 (BS2), S1.16 (R/W#), S1.17 (E/RD#), S1.21 (D8), S1.22 (D4), S1.23 (D5), S1.24 (D6), S1.25 (D7), S1.29 (SDA), S1.30 (NC_(GND)), SW1.2, SW2.2, SW3.2, U1.4 (SHDN), U1.6 (AGND), U1.7 (GND), U3.2 (GND), U5.5 (GNDANA), U5.18 (GND), U5.35 (GND), U5.42 (GND), U6.4 (V-), U7.2 (CATHODE), U7.3 (CATHODE), U8.2 (CATHODE), U8.3 (CATHODE), U9.2 (CATHODE), U9.3 (CATHODE), U10.3, U12.3, U14.1 (GND), U15.4 (VSS), U16.7 (GND)
GND_C: C13.2, C18.2, C19.2, C35.2, C36.2, D4.2 (A), D5.2 (A2), J3.22, J3.23, P12.1, U7.5, U8.5, U9.5, U12.4
JOY: JS2.4 (B_(right)), R18.1, R19.2, U5.10 (EXTINT5EXTWAKE5/AIN5/AIN1/VOUT1/OAPOS2/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)
LE: R37.2, U5.15 (EXTINT10/AIN18/X2Y8/SERCOM0PAD2/SERCOM2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)
LE_C: D4.1 (K1), FB3.1, J3.10
unnamed: C1.1, C2.1, L1.1, R7.1, SW5.1, U1.2 (VCC)
unnamed: C3.1, U1.5 (REF)
unnamed: C7.1, S1.2 (C2P)
unnamed: C7.2, S1.3 (C2N)
unnamed: C8.1, S1.28 (VCC)
unnamed: C9.1, S1.4 (C1P)
unnamed: C9.2, S1.5 (C1N)
unnamed: C10.1, S1.27 (VCOMH)
unnamed: C11.1, R12.1, R13.1
unnamed: C11.2, U3.3 (IN)
unnamed: C16.1, C17.2, R31.2, U6.2 (-)
unnamed: C20.1, U5.43 (VSW)
unnamed: C23.2, U5.1 (XIN32/EXTINT0EXTWAKE0/SERCOM1PAD0/TCC2W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), Y1.1
unnamed: C25.2, U5.2 (XOUT32/EXTINT1EXTWAKE1/SERCOM1PAD1/TCC2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), Y1.2
unnamed: C28.2, D2.2 (A), R10.2, U16.1
unnamed: C29.2, D3.1 (K), R44.2, U16.9
unnamed: C31.2, R11.1, R29.2, U16.3
unnamed: C37.2, FB3.2, U7.6 (COLLECTOR)
unnamed: D1.2 (A), L1.2, T1.2 (D)
unnamed: D2.1 (K), D3.2 (A), R10.1, R44.1, U16.4
unnamed: FB1.2, U7.7 (COLLECTOR)
unnamed: FB2.2, U8.7 (COLLECTOR)
unnamed: FB4.2, U8.6 (COLLECTOR)
unnamed: FB5.2, U9.7 (COLLECTOR)
unnamed: FB6.1, J3.18
unnamed: FB8.1, J3.20
unnamed: J1.A5 (CC1), R47.1
unnamed: J1.B5 (CC2), R46.1
unnamed: JS2.1 (A_(up)), R21.1
unnamed: JS2.3 (C_(left)), R20.1, R21.2
unnamed: JS2.6 (D_(down)), R19.1, R20.2
unnamed: LED1.2 (A), R6.2
unnamed: LED2.2 (A), R4.2
unnamed: LED3.2 (A), R8.2
unnamed: R1.1, R9.2, U15.7 (PB0)
unnamed: R2.2, U1.3 (FB), U15.5 (PA0), U15.6 (PW0)
unnamed: R3.1, S1.26 (REF)
unnamed: R22.2, R30.1, U6.5 (+)
unnamed: R32.1, U7.1 (ANODE)
unnamed: R34.1, U9.1 (ANODE)
unnamed: R36.1, U8.1 (ANODE)
unnamed: R37.1, U7.4 (ANODE)
unnamed: R40.1, U8.4 (ANODE)
unnamed: R41.1, U9.4 (ANODE)
unnamed: R45.1, U10.1
unnamed: R48.1, U11.1
unnamed: R49.1, U12.1
unnamed: R51.1, U13.1
unnamed: RSENSE1.1, T1.3 (S), U1.8 (CS)
unnamed: SP1.1, U3.1 (OUT-)
unnamed: SP1.2, U3.6 (OUT+)
unnamed: T1.1 (G), U1.1 (EXT)
unnamed: U6.3 (+), U6.6 (-), U6.7
unnamed: U10.2, U16.2
unnamed: U11.2, U16.6
unnamed: U12.2, U16.12
unnamed: U13.2, U16.10
unnamed: U16.5, U16.8, U16.11, U16.13
POL: R36.2, U5.23 (XIN/EXTINT14/SERCOM2PAD2/SERCOM4PAD2/TC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)
POL_C: D4.5 (K4), FB2.1, J3.8
RESET: J2.10, R5.1, SW3.1, U5.40 (~RESET~)
RX_LED: R6.1, U5.48 (EXTINT3/AIN11/SERCOM5PAD1/TC2WO1/SUPCVB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)
SENS_PAD: J3.16, U5.27 (EXTINT2/X6/SERCOM1PAD2/SERCOM3PAD2/TC4W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)
SPK: R12.2, U5.3 (EXTINT2EXTWAKE2/AIN0/Y0/VOUT0/OANEG0/PA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)
SW1: SW1.1, U5.11 (EXTINT6EXTWAKE6/AIN6/AIN2/Y4/OAPOS0/SER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)
SW2: SW2.1, U5.29 (EXTINT4/X8/SERCOM5PAD2/SERCOM3PAD2/TC3W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)
SW3: JS2.2 (Center), U5.30 (EXTINT5/X9/SERCOM5PAD3/SERCOM3PAD3/TC3W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)
SWCLK: J2.4, U5.45 (EXTINT10/SERCOM1PAD2/TCC1WO0/CORTEXM0PS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)
SWDIO: J2.2, U5.46 (EXTINT11/SERCOM1PAD3/TCC1WO1/SWDIO/CCL1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)
VDD_C: C13.1, C19.1, C36.1, C37.1, D5.1 (A1), FB6.2, U7.8 (VCC), U8.8 (VCC), U9.8 (VCC), U13.3
VSENS: R9.1, U5.9 (EXTINT4EXTWAKE4/VREFB/AIN4/AIN0/OAOUT2/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)
V_CS: U5.22 (ACCMP1/TC2WO1/SERCOM4P1/SERCOM2P1/PA13), U15.1 (~CS)
V_GND: C16.2, J3.2, P1.1
V_HV: C4.1, C6.1, D1.1 (K), R2.1, U11.4
V_HV_C: C18.1, C35.1, FB8.2, P7.1, U10.4, U11.3
V_SCK: U5.28 (EXTINT3/X7/SERCOM1PAD3/SERCOM3PAD3/TC4W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), U15.2 (SCK)
V_SI: U5.25 (EXTINT0/X4/SERCOM1PAD0/SERCOM3PAD4/TCC2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), U15.3 (SI)
V_USB: C5.1, C27.2, J1.A4 (VBUS), J1.A9 (VBUS), J1.B4 (VBUS), J1.B9 (VBUS), R45.2, R48.2, R49.2, R51.2, SW5.2, U13.4, U14.3 (VI), U16.14 (VCC)
V_USB_SENS: R7.2, R14.1, U5.47 (EXTINT2/AIN10/SERCOM5PAD0/TC2WO0/SUPCOU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)

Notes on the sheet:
VOUT = 1.5 x (R2/R1 +1)
Display
AC SWITCHER
HIGH VOLTAGE BOOST CONVERTER
FEEDBACK AMPLIFIER
INTERFACE
HIGH VOLTAGE DRIVER
OPTO ISOLATORS
MICROCONTROLLER
OLED DISPLAY
D6 / changed
A0 / vout
changed
50k
D3 / changed
LED? MKR
A3 / A3? MKR
A4? MKR
D8 / A5? MKR
D9 / A6? MKR
D4 / SDA? MKR
SCL? MKR
D1 / PWM2? MKR
D0 / PWM3? MKR
D23 / PWM4? MKR
D24 / PWM5? MKR
22/ MOSI? MKR
? / SCK? MKR
D2 / DATA? MKR
MISO? MKR
MOSI? MKR / SERCOM 1
SCK? MKR / SERCOM1
D10 / USB_PAD4??? MKR / SERCOM1
MISO? MKR / SERCOM1
PAD6? MKR
D7 / PAD7? MKR
PAD7? MKR
PAD0? MKR
TX? MKR
RX? MKR



Board: 2 copper layers, 124.0 x 115.4 mm, 122 parts (107 on the bottom side), 104 nets.

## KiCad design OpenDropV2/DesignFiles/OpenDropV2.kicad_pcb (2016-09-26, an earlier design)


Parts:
C1: 100uF, 35V; R_2512_HandSoldering
C2, C3, C11, C12, C13, C14: 100nF; C_0805
C4: 4u7, 250V; C_SMD_12mm
C5: 10uF, 25V; C_1210_HandSoldering
C6: 100nF, 250V; C100n_250V
C7, C9, C15, C16: 1uF; C_0805
C8, C10: 2.2uF; C_0805
C17: 1pF; C_0805
D1: ES2F; DO-214AA
D2, D3, D4, D5: 1N4148; SOD-323
FLUXL1, FLUXL2, FLUXL3, FLUXL4, FLUXL5, FLUXL6, FLUXL7, FLUXL8, FLUXL9, FLUXL10, FLUXL11, FLUXL12, FLUXL13, FLUXL14, FLUXL15, FLUXL16, FLUXL17, FLUXL18, FLUXL19, FLUXL20, FLUXL21, FLUXL22, FLUXL23, FLUXL24, FLUXL25, FLUXL26, FLUXL27, FLUXL28, FLUXL29, FLUXL30, FLUXL31, FLUXL32, FLUXL33, FLUXL34, FLUXL35, FLUXL36, FLUXL37, FLUXL38, FLUXL39, FLUXL40, FLUXL41, FLUXL42, FLUXL43, FLUXL44, FLUXL45, FLUXL46, FLUXL47, FLUXL48, FLUXL49, FLUXL50, FLUXL51, FLUXL52, FLUXL53, FLUXL54, FLUXL55, FLUXL56, FLUXL57, FLUXL58, FLUXL59, FLUXL60, FLUXL61, FLUXL62, FLUXL63, FLUXL64, FLUXL65, FLUXL66, FLUXL67, FLUXL68, FLUXL69, FLUXL70, FLUXL71, FLUXL72, FLUXL73, FLUXL74, FLUXL75, FLUXL76, FLUXL77, FLUXL78, FLUXL79, FLUXL80, FLUXL81, FLUXL82, FLUXL83, FLUXL84, FLUXL85, FLUXL86, FLUXL87, FLUXL88, FLUXL89, FLUXL90, FLUXL91, FLUXL92, FLUXL93, FLUXL94, FLUXL95, FLUXL96, FLUXL97, FLUXL98, FLUXL99, FLUXL100, FLUXL101, FLUXL102, FLUXL103, FLUXL104, FLUXL105, FLUXL106, FLUXL107, FLUXL108, FLUXL109, FLUXL110, FLUXL111, FLUXL112, FLUXL113, FLUXL114, FLUXL115, FLUXL116, FLUXL117, FLUXL118, FLUXL119, FLUXL120, FLUXL121, FLUXL122, FLUXL123, FLUXL124, FLUXL125, FLUXL126, FLUXL127, FLUXL128: FX; FLUXPAD_2_75_4MIL_4_5
J1: DC_JACK; DC_JACK_SMD
JS1: JoystickSMD; JoystickSMD_SKQUSeries
L1: 100uH; Inductor_18.54x15.24
LED1, LED8: LED; LED-0805
LED2, LED3, LED4, LED5: LED; LED_SIDE
P1, P2, P3, P5, P7, P8, P9, P10, P11, P12: CONN_01X01; Measurement_Point_Square-SMD-Pad_Small
P6: CONN_01X30; OLED_SolderPads
P13: ScrewPad1; MountingHolePad_3x9mm
P14: ScrewPad2; MountingHolePad_3x9mm
P15: ScrewPad3; MountingHolePad_3x9mm
P16: ScrewPad4; MountingHolePad_3x9mm
POT1: 5k Ohm; Potentiometer_Trimmer-Suntan-TSR-3386P
Q1, Q2, Q3, Q5, Q6, Q7: BSS138; SOT-23
R1: 8k; R_0805
R2: 1M5; R_2512
R3: 390k; R_0805
R4, R6: 390; R_0805
R5: 10; R_0805
R7, R15, R16, R17: 10k; R_0805_HeatPad
R8, R9, R10, R11, R12, R13, R14, R18, R19, R20, R21, R22, R23, R24, R25, R26, R27, R28, R29, R30: 10k; R_0805
R31: 200k; R_0805
RSENSE1: 0R050; R_2010
S1: OLED_DISPLAY; OLED_096_1
SP1: SPEAKER; SMD_PA12_Piezzo
SW1, SW2: SW_PUSH; PUSH_BUTTON_SMD
SW5: SPST; Switch_On-On
T1: IRF 840S; D2PAK
U1: MAX1771ESA; SO08
U2, U4: HV507; PQFP-80_14x20mm_Pitch0.8mm
U3: ARDUINO_MICRO; ARDUINO_MICRO_SMD
U5: ESP8266_SMD
U6: MCP6002; SO08

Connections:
3.3V: C11.1, C14.1, D5.1 (K), P6.6, P6.9, Q1.1 (G), Q2.1 (G), Q5.1 (G), Q6.1 (G), Q7.1 (G), R10.1, R11.1, R12.1, R13.1, R14.1, R25.2, R26.2, R27.2, S1.6 (VBAT), S1.9 (VDD), U3.19 (3.3V), U5.4 (CH_PD), U5.8 (VCC)
CLK: P11.1, U2.37 (CLK), U3.34 (SCK), U4.37 (CLK)
DI: U3.1 (MOSI), U4.26 (DIO_A)
DIO_B: P9.1, U2.39 (DIO_B)
DISP_CS: D2.1 (K), U3.17 (12/A11)
DISP_DC: D4.1 (K), U3.16 (11(PWM))
DISP_RES: D3.1 (K), U3.18 (13(PWM))
DISP_SCL: Q1.3 (D), R9.2, U3.8 (3(PWM)/SCL)
DISP_SDA: Q2.3 (D), R8.2, U3.7 (2/SDA)
ESP_GPIO0: Q5.3 (D), R23.1, U3.15 (10(PWM)/A10)
ESP_RESET: Q7.3 (D), R28.1, U3.24 (A3)
ESP_RX: R24.1, U3.3 (1/TX)
ESP_TX: Q6.3 (D), R29.1, U3.4 (0/RX)
FEEDBACK: C17.1, R31.1, U3.23 (A2), U6.1
GND: C1.2, C2.2, C3.2, C4.2, C5.2, C6.2, C8.2, C10.2, C11.2, C12.2, C13.2, C14.2, C15.2, J1.1, J1.2, JS1.4 (Common), LED1.1 (K), LED2.1 (K), LED3.1 (K), LED4.1 (K), LED5.1 (K), LED8.1 (K), P5.1, P6.8, P6.10, P6.11, P6.12, P6.16, P6.17, P6.21, P6.22, P6.23, P6.24, P6.25, P6.29, P6.30, P12.1, R1.2, R3.2, R30.2, RSENSE1.2, S1.8 (VSS), S1.10 (BS0), S1.11 (BS1), S1.12 (BS2), S1.16 (R/W#), S1.17 (E/RD#), S1.21 (D8), S1.22 (D4), S1.23 (D5), S1.24 (D6), S1.25 (D7), S1.29 (SDA), S1.30 (NC_(GND)), SP1.1, SW1.2, SW2.2, U1.4 (SHDN), U1.6 (AGND), U1.7 (GND), U2.32 (DIR), U2.33 (GND), U2.34 (HVGND), U3.6 (GND), U3.31 (GND), U4.32 (DIR), U4.33 (GND), U4.34 (HVGND), U5.1 (GND), U6.4 (V-)
JOY: JS1.5 (D_(rigth)), R18.1, R19.2, U3.25 (A4)
LE: P8.1, U2.38 (LE), U3.9 (4/A6), U4.38 (LE)
LED_LIGHT: Q3.1 (G), U3.10 (5(PWM))
unnamed: C1.1, C2.1, C5.1, L1.1, SW5.1, U1.2 (VCC)
unnamed: C3.1, U1.5 (REF)
unnamed: C7.1, P6.2, S1.2 (C2P)
unnamed: C7.2, P6.3, S1.3 (C2N)
unnamed: C8.1, P6.28, S1.28 (VCC)
unnamed: C9.1, P6.4, S1.4 (C1P)
unnamed: C9.2, P6.5, S1.5 (C1N)
unnamed: C10.1, P6.27, S1.27 (VCOMH)
unnamed: C16.1, C17.2, R31.2, U6.2 (-)
unnamed: D1.2 (A), L1.2, T1.2 (D)
unnamed: D2.2 (A), P6.13, R11.2, S1.13 (CS)
unnamed: D3.2 (A), P6.14, R10.2, S1.14 (RES)
unnamed: D4.2 (A), P6.15, R14.2, S1.15 (D/C#_SA0)
unnamed: D5.2 (A), R24.2, U5.7 (RX)
unnamed: FLUXL1.1, U2.44 (HV_OUT_4)
unnamed: FLUXL2.1, U2.47 (HV_OUT_7)
unnamed: FLUXL3.1, U2.51 (HV_OUT_11)
unnamed: FLUXL4.1, U2.54 (HV_OUT_14)
unnamed: FLUXL5.1, U2.58 (HV_OUT_18)
unnamed: FLUXL6.1, U2.61 (HV_OUT_21)
unnamed: FLUXL7.1, U2.65 (HV_OUT_25)
unnamed: FLUXL8.1, U2.70 (HV_OUT_30)
unnamed: FLUXL9.1, U2.43 (HV_OUT_3)
unnamed: FLUXL10.1, U2.48 (HV_OUT_8)
unnamed: FLUXL11.1, U2.50 (HV_OUT_10)
unnamed: FLUXL12.1, U2.55 (HV_OUT_15)
unnamed: FLUXL13.1, U2.59 (HV_OUT_19)
unnamed: FLUXL14.1, U2.62 (HV_OUT_22)
unnamed: FLUXL15.1, U2.69 (HV_OUT_29)
unnamed: FLUXL16.1, U2.66 (HV_OUT_26)
unnamed: FLUXL17.1, U2.42 (HV_OUT_2)
unnamed: FLUXL18.1, U2.46 (HV_OUT_6)
unnamed: FLUXL19.1, U2.52 (HV_OUT_12)
unnamed: FLUXL20.1, U2.56 (HV_OUT_16)
unnamed: FLUXL21.1, U2.60 (HV_OUT_20)
unnamed: FLUXL22.1, U2.63 (HV_OUT_23)
unnamed: FLUXL23.1, U2.68 (HV_OUT_28)
unnamed: FLUXL24.1, U2.67 (HV_OUT_27)
unnamed: FLUXL25.1, U2.41 (HV_OUT_1)
unnamed: FLUXL26.1, U2.45 (HV_OUT_5)
unnamed: FLUXL27.1, U2.49 (HV_OUT_9)
unnamed: FLUXL28.1, U2.53 (HV_OUT_13)
unnamed: FLUXL29.1, U2.57 (HV_OUT_17)
unnamed: FLUXL30.1, U2.64 (HV_OUT_24)
unnamed: FLUXL31.1, U2.72 (HV_OUT_32)
unnamed: FLUXL32.1, U2.71 (HV_OUT_31)
unnamed: FLUXL33.1, U2.24 (HV_OUT_64)
unnamed: FLUXL34.1, U2.20 (HV_OUT_60)
unnamed: FLUXL35.1, U2.16 (HV_OUT_56)
unnamed: FLUXL36.1, U2.12 (HV_OUT_52)
unnamed: FLUXL37.1, U2.8 (HV_OUT_48)
unnamed: FLUXL38.1, U2.1 (HV_OUT_41)
unnamed: FLUXL39.1, U2.73 (HV_OUT_33)
unnamed: FLUXL40.1, U2.74 (HV_OUT_34)
unnamed: FLUXL41.1, U2.23 (HV_OUT_63)
unnamed: FLUXL42.1, U2.19 (HV_OUT_59)
unnamed: FLUXL43.1, U2.13 (HV_OUT_53)
unnamed: FLUXL44.1, U2.9 (HV_OUT_49)
unnamed: FLUXL45.1, U2.5 (HV_OUT_45)
unnamed: FLUXL46.1, U2.2 (HV_OUT_42)
unnamed: FLUXL47.1, U2.78 (HV_OUT_38)
unnamed: FLUXL48.1, U2.77 (HV_OUT_37)
unnamed: FLUXL49.1, U2.22 (HV_OUT_62)
unnamed: FLUXL50.1, U2.17 (HV_OUT_57)
unnamed: FLUXL51.1, U2.15 (HV_OUT_55)
unnamed: FLUXL52.1, U2.10 (HV_OUT_50)
unnamed: FLUXL53.1, U2.6 (HV_OUT_46)
unnamed: FLUXL54.1, U2.3 (HV_OUT_43)
unnamed: FLUXL55.1, U2.76 (HV_OUT_36)
unnamed: FLUXL56.1, U2.79 (HV_OUT_39)
unnamed: FLUXL57.1, U2.21 (HV_OUT_61)
unnamed: FLUXL58.1, U2.18 (HV_OUT_58)
unnamed: FLUXL59.1, U2.14 (HV_OUT_54)
unnamed: FLUXL60.1, U2.11 (HV_OUT_51)
unnamed: FLUXL61.1, U2.7 (HV_OUT_47)
unnamed: FLUXL62.1, U2.4 (HV_OUT_44)
unnamed: FLUXL63.1, U2.80 (HV_OUT_40)
unnamed: FLUXL64.1, U2.75 (HV_OUT_35)
unnamed: FLUXL65.1, U4.41 (HV_OUT_1)
unnamed: FLUXL66.1, U4.42 (HV_OUT_2)
unnamed: FLUXL67.1, U4.43 (HV_OUT_3)
unnamed: FLUXL68.1, U4.44 (HV_OUT_4)
unnamed: FLUXL69.1, U4.45 (HV_OUT_5)
unnamed: FLUXL70.1, U4.46 (HV_OUT_6)
unnamed: FLUXL71.1, U4.47 (HV_OUT_7)
unnamed: FLUXL72.1, U4.48 (HV_OUT_8)
unnamed: FLUXL73.1, U4.49 (HV_OUT_9)
unnamed: FLUXL74.1, U4.50 (HV_OUT_10)
unnamed: FLUXL75.1, U4.51 (HV_OUT_11)
unnamed: FLUXL76.1, U4.52 (HV_OUT_12)
unnamed: FLUXL77.1, U4.53 (HV_OUT_13)
unnamed: FLUXL78.1, U4.54 (HV_OUT_14)
unnamed: FLUXL79.1, U4.55 (HV_OUT_15)
unnamed: FLUXL80.1, U4.56 (HV_OUT_16)
unnamed: FLUXL81.1, U4.57 (HV_OUT_17)
unnamed: FLUXL82.1, U4.58 (HV_OUT_18)
unnamed: FLUXL83.1, U4.59 (HV_OUT_19)
unnamed: FLUXL84.1, U4.60 (HV_OUT_20)
unnamed: FLUXL85.1, U4.61 (HV_OUT_21)
unnamed: FLUXL86.1, U4.62 (HV_OUT_22)
unnamed: FLUXL87.1, U4.63 (HV_OUT_23)
unnamed: FLUXL88.1, U4.64 (HV_OUT_24)
unnamed: FLUXL89.1, U4.65 (HV_OUT_25)
unnamed: FLUXL90.1, U4.66 (HV_OUT_26)
unnamed: FLUXL91.1, U4.67 (HV_OUT_27)
unnamed: FLUXL92.1, U4.68 (HV_OUT_28)
unnamed: FLUXL93.1, U4.69 (HV_OUT_29)
unnamed: FLUXL94.1, U4.70 (HV_OUT_30)
unnamed: FLUXL95.1, U4.71 (HV_OUT_31)
unnamed: FLUXL96.1, U4.72 (HV_OUT_32)
unnamed: FLUXL97.1, U4.73 (HV_OUT_33)
unnamed: FLUXL98.1, U4.74 (HV_OUT_34)
unnamed: FLUXL99.1, U4.75 (HV_OUT_35)
unnamed: FLUXL100.1, U4.76 (HV_OUT_36)
unnamed: FLUXL101.1, U4.77 (HV_OUT_37)
unnamed: FLUXL102.1, U4.78 (HV_OUT_38)
unnamed: FLUXL103.1, U4.79 (HV_OUT_39)
unnamed: FLUXL104.1, U4.80 (HV_OUT_40)
unnamed: FLUXL105.1, U4.1 (HV_OUT_41)
unnamed: FLUXL106.1, U4.2 (HV_OUT_42)
unnamed: FLUXL107.1, U4.3 (HV_OUT_43)
unnamed: FLUXL108.1, U4.4 (HV_OUT_44)
unnamed: FLUXL109.1, U4.5 (HV_OUT_45)
unnamed: FLUXL110.1, U4.6 (HV_OUT_46)
unnamed: FLUXL111.1, U4.7 (HV_OUT_47)
unnamed: FLUXL112.1, U4.8 (HV_OUT_48)
unnamed: FLUXL113.1, U4.9 (HV_OUT_49)
unnamed: FLUXL114.1, U4.10 (HV_OUT_50)
unnamed: FLUXL115.1, U4.11 (HV_OUT_51)
unnamed: FLUXL116.1, U4.12 (HV_OUT_52)
unnamed: FLUXL117.1, U4.13 (HV_OUT_53)
unnamed: FLUXL118.1, U4.14 (HV_OUT_54)
unnamed: FLUXL119.1, U4.15 (HV_OUT_55)
unnamed: FLUXL120.1, U4.16 (HV_OUT_56)
unnamed: FLUXL121.1, U4.17 (HV_OUT_57)
unnamed: FLUXL122.1, U4.18 (HV_OUT_58)
unnamed: FLUXL123.1, U4.19 (HV_OUT_59)
unnamed: FLUXL124.1, U4.20 (HV_OUT_60)
unnamed: FLUXL125.1, U4.21 (HV_OUT_61)
unnamed: FLUXL126.1, U4.22 (HV_OUT_62)
unnamed: FLUXL127.1, U4.23 (HV_OUT_63)
unnamed: FLUXL128.1, U4.24 (HV_OUT_64)
unnamed: JS1.1 (A_(up)), R21.1
unnamed: JS1.2 (B_(left)), R20.1, R21.2
unnamed: JS1.3 (C_(down)), R19.1, R20.2
unnamed: LED1.2 (A), R4.2
unnamed: LED2.2 (A), LED3.2 (A), LED4.2 (A), LED5.2 (A), Q3.2 (S)
unnamed: LED8.2 (A), R6.2
unnamed: P2.1, U3.22 (A1)
unnamed: P6.18, Q1.2 (S), R13.2, S1.18 (D0_(SCL))
unnamed: P6.19, Q2.2 (S), R12.2, S1.19 (D1_(SA))
unnamed: P6.26, R3.1, S1.26 (REF)
unnamed: POT1.1, POT1.2, R1.1
unnamed: POT1.3, R2.2, U1.3 (FB)
unnamed: Q3.3 (D), R5.1
unnamed: Q5.2 (S), R25.1, U5.5 (GPIO-0)
unnamed: Q6.2 (S), R26.1, U5.2 (TX)
unnamed: Q7.2 (S), R27.1, U5.6 (RESET)
unnamed: R22.2, R30.1, U6.5 (+)
unnamed: RSENSE1.1, T1.3 (S), U1.8 (CS)
unnamed: T1.1 (G), U1.1 (EXT)
unnamed: U2.26 (DIO_A), U4.39 (DIO_B)
unnamed: U6.3 (+), U6.6 (-), U6.7
RX_LED: R6.1, U3.2 (RX_LED/SS)
SPK: SP1.2, U3.11 (6(PWM)/A7)
SW1: SW1.1, U3.13 (8/A8)
SW2: SW2.1, U3.26 (A5)
SW3: JS1.6 (Center), U3.12 (7)
VIN: J1.3, SW5.2, U3.32 (VIN)
V_GND: C16.2, P1.1, P13.1
V_HV: C4.1, C6.1, D1.1 (K), P7.1, R2.1, U2.25 (VPP), U4.40 (VPP)

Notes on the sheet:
65-260VDC
High Voltage Generator
Fluxl Drivers
Controller & WIFI
Display
Level Shifters
LEDs & Switches

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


Board: 2 copper layers, 100.0 x 100.0 mm, 225 parts (77 on the bottom side), 191 nets.

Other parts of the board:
P13#2, P13#3, P13#4: ScrewPad1; MountingHolePad_3x9mm

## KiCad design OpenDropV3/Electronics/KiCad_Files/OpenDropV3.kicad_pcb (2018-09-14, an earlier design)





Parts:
C1: 100uF, 35V; C_2512_HandSoldering
C2, C3, C12, C13, C14, C22, C26, C30, C31, C33, C34, C36: 100nF; C_0805
C4, C18: 4u7, 250V; c_elec_10x10
C5, C21: 22uF; C_1206
C6, C35: 100nF, 250V; C_1913
C7, C9, C11, C15, C16, C20, C24, C27: 1uF; C_0805
C8, C10: 2.2uF; C_0805
C17: 1pF; C_0805
C19: 22uF, 50V; c_elec_6.3x5.8
C23, C25: 22pF; C_0805
C28, C29: 3.3nF; C_0805
C32: 100uF,35V; C_2512_HandSoldering
C37: 470pF; C_0805
D1: ES2F; DO-214AA
D2, D3: 1N4148; D_SOD-323
FLUXL_1_1, FLUXL_1_8, FLUXL_16_1, FLUXL_16_8: FX; FLUXPAD_2_75_4MIL_4_5_res1
FLUXL_1_2, FLUXL_1_7, FLUXL_16_2, FLUXL_16_7: FX; FLUXPAD_2_75_4MIL_4_5_res4
FLUXL_1_2b1, FLUXL_1_7b1, FLUXL_16_2b1, FLUXL_16_7b1: FX; FLUXPAD_2_75_4MIL_4_5_res5
FLUXL_1_3, FLUXL_1_6, FLUXL_16_3, FLUXL_16_6: FX; FLUXPAD_2_75_4MIL_4_5_res2
FLUXL_1_4, FLUXL_1_5, FLUXL_16_4, FLUXL_16_5: FX; FLUXPAD_2_75_4MIL_4_5_res3
FLUXL_2_1, FLUXL_15_8: FX; FLUXPAD_2_75_4MIL_4_5_topleft
FLUXL_2_2, FLUXL_2_7, FLUXL_3_2, FLUXL_3_3, FLUXL_3_4, FLUXL_3_5, FLUXL_3_6, FLUXL_3_7, FLUXL_4_2, FLUXL_4_3, FLUXL_4_4, FLUXL_4_5, FLUXL_4_6, FLUXL_4_7, FLUXL_5_2, FLUXL_5_3, FLUXL_5_4, FLUXL_5_5, FLUXL_5_6, FLUXL_5_7, FLUXL_6_2, FLUXL_6_3, FLUXL_6_4, FLUXL_6_5, FLUXL_6_6, FLUXL_6_7, FLUXL_7_2, FLUXL_7_3, FLUXL_7_4, FLUXL_7_5, FLUXL_7_6, FLUXL_7_7, FLUXL_8_2, FLUXL_8_3, FLUXL_8_4, FLUXL_8_5, FLUXL_8_6, FLUXL_8_7, FLUXL_9_2, FLUXL_9_3, FLUXL_9_4, FLUXL_9_5, FLUXL_9_6, FLUXL_9_7, FLUXL_10_2, FLUXL_10_3, FLUXL_10_4, FLUXL_10_5, FLUXL_10_6, FLUXL_10_7, FLUXL_11_2, FLUXL_11_3, FLUXL_11_4, FLUXL_11_5, FLUXL_11_6, FLUXL_11_7, FLUXL_12_2, FLUXL_12_3, FLUXL_12_4, FLUXL_12_5, FLUXL_12_6, FLUXL_12_7, FLUXL_13_2, FLUXL_13_3, FLUXL_13_4, FLUXL_13_5, FLUXL_13_6, FLUXL_13_7, FLUXL_14_2, FLUXL_14_3, FLUXL_14_4, FLUXL_14_5, FLUXL_14_6, FLUXL_14_7, FLUXL_15_2, FLUXL_15_7: FX; FLUXPAD_2_75_4MIL_4_5
FLUXL_2_3, FLUXL_2_4, FLUXL_2_5, FLUXL_2_6, FLUXL_15_3, FLUXL_15_4, FLUXL_15_5, FLUXL_15_6: FX; FLUXPAD_2_75_4MIL_4_5_side
FLUXL_2_8, FLUXL_15_1: FX; FLUXPAD_2_75_4MIL_4_5_topright
FLUXL_3_1, FLUXL_3_8, FLUXL_4_1, FLUXL_4_8, FLUXL_5_1, FLUXL_5_8, FLUXL_6_1, FLUXL_6_8, FLUXL_7_1, FLUXL_7_8, FLUXL_8_1, FLUXL_8_8, FLUXL_9_1, FLUXL_9_8, FLUXL_10_1, FLUXL_10_8, FLUXL_11_1, FLUXL_11_8, FLUXL_12_1, FLUXL_12_8, FLUXL_13_1, FLUXL_13_8, FLUXL_14_1, FLUXL_14_8: FX; FLUXPAD_2_75_4MIL_4_5_top
J1: USB_C_Receptacle; USB_C_Receptacle_Amphenol_12401610E4-2A
J2: Conn_02x05_Odd_Even; Pin_Header_Straight_2x05_Pitch1.27mm_SMD
JS1: JoystickSMD; JoystickSMD_SKQUSeries
JS2: JoystickSMD_SKRH; SKRHABE010
L1: 100uH; SRN1060
LED1, LED2, LED3: LED; LED-0805
P1, P3, P7, P8, P9, P10, P11, P12: CONN_01X01; Measurement_Point_Square-SMD-Pad_Small
P2: ScrewPad4; Measurement_Point_Croki
P4: CONN_PSEUDO_AC; Measurement_Point_Square-SMD-Pad_Small
P13: ScrewPad1; MountingHolePad_3x9mm
P14: ScrewPad2; MountingHolePad_3x9mm
P15: ScrewPad3; MountingHolePad_3x9mm
P16: ScrewPad4; MountingHolePad_3x9mm
R1: 6.8k; R_0805
R2: 1M5; R_2512
R3, R9: 390k; R_0805
R4, R6, R8, R13: 390; R_0805
R5, R10, R18, R19, R20, R21, R22, R30, R44: 10k; R_0805
R7, R15, R16, R17: 10R; R_0805_HeatPad
R11, R31: 15k; R_0805
R12, R33, R35, R38, R42, R43: 2.2k; R_0805
R14, R23, R24, R25, R26, R27, R28: 0k; R_0805
R29: 680k?; R_0805
R32, R34, R36, R37, R40, R41, R45, R48, R49, R51: 220; R_0805
R39: 5.6k; R_0805
R46, R47: 5k; R_0805
RSENSE1: 0R1; R_2010
S1: OLED_DISPLAY; OLED_096_1_Flip
SP1: SPEAKER; Speaker16mm
SW1, SW2: SW_PUSH; PUSH_BUTTON_SMD
SW3: SW_PUSH; SW_SPST_KMS221GLFS
SW5: SPST; Switch_On-On
T1: TK560P60Y; D-Pak_TO252AA
U1: MAX1771ESA; SO08
U2, U4: HV507; PQFP-80_14x20mm_Pitch0.8mm
U3: PAM8301; SOT-23-6
U5: SAMD21G18B-A changed from SAML21; TQFP-48_7x7mm_Pitch0.5mm
U6: MCP6002; SO08
U7, U8, U9: HCPL0534; HCPL_Optocoupler_SMD
U10, U11, U12, U13: AQY210EH; SMD_DIP4
U14: TLV1117-33; SOT-223
U15: MCP41010; SO08
U16: 74xx14; SOIC-14_N
Y1: 32.765; Crystal_SMD_3215-2pin_3.2x1.5mm

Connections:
+3V3: C14.1, C15.1, C21.1, C22.2, C26.1, C30.1, C33.2, C34.2, J2.1, R4.1, R5.2, R11.2, R18.2, R22.1, S1.6 (VBAT), S1.9 (VDD), U3.4 (~SD), U3.5 (VDD), U5.6 (VDDANA), U5.17 (VDDIO), U5.36 (VDDIO), U5.44 (VDDIN), U6.8 (V+), U14.2 (VO), U15.8 (VDD)
AC: C31.1, U5.7 (EXTINT8/AIN2/OAOUT1/SERCOM4PAD0/TC0WO0/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)
AREF: C24.2, U5.4 (Y1/AIN1/VREFA/VREFP/PA03)
BL: R40.2, U5.12 (EXTINT7EXTWAKE7/AIN7/AIN3/OAOUT0/SERCOM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)
BL_C: R23.1, R25.2, U4.29 (BL)
BL_C2: P10.1, R23.2, U2.29 (BL)
CLK: R32.2, U5.20 (EXTINT11/Y3/SERCOM4PAD3/TC1WO1/TCC0WO5/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)
CLK_C: P11.1, R33.1, U2.37 (CLK), U4.37 (CLK), U7.7 (COLLECTOR)
D13: R8.1, U5.26 (EXTINT1/X5/SERCOM1PAD1/SERCOM3PAD1/TCC2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)
D+: J1.A6 (D+), J1.B6 (D+), U5.34 (EXTINT13/SERCOM3PAD3/SERCOM5PAD3/TC1WO1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)
D-: J1.A7 (D-), J1.B7 (D-), U5.33 (EXTINT12/SERCOM3PAD2/SERCOM5PAD2/TC1WO1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)
DI: R34.2, U5.19 (EXTINT10/Y2/SERCOM4PAD2/TC1WO0/TCC0WO4/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)
DIO_B: P9.1, U2.39 (DIO_B)
DISP_CS: S1.13 (CS), U5.21 (ACCMP0/TC2WO0/SERCOM4P0/SERCOM2P0/PA12)
DISP_DC: S1.15 (D/C#_SA0), U5.16 (EXTINT11/AIN19/X3Y9/SERCOM0PAD3/SERCOM2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)
DISP_RES: S1.14 (RES), U5.24 (XOUT/EXTINT15/SERCOM2PAD3/SERCOM4PAD3/T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)
DISP_SCL: S1.18 (D0_(SCL)), U5.32 (EXTINT7/X11/SERCOM3PAD1/SERCOM5PAD1/TC0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)
DISP_SDA: S1.19 (D1_(SA)), U5.31 (EXTINT6/X10/SERCOM3PAD0/SERCOM5PAD0/TC0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)
DI_C: R24.2, U4.26 (DIO_A)
FEEDBACK: C17.1, R31.1, U5.8 (EXTINT9/AIN3/Y15/OAPOS1/SERCOM4PAD1/TC0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), U6.1
GND: C1.2, C2.2, C3.2, C4.2, C5.2, C6.2, C8.2, C10.2, C14.2, C15.2, C20.2, C21.2, C22.1, C23.1, C24.1, C25.1, C26.2, C27.1, C28.1, C29.1, C30.2, C32.2, C33.1, C34.1, J1.A1 (GND), J1.A12 (GND), J1.B1 (GND), J1.B12 (GND), J2.3, J2.5, J2.9, JS1.4 (Common), JS2.5 (Common), LED1.1 (K), LED2.1 (K), LED3.1 (K), P2.1, P13.1, R1.2, R3.2, R13.2, R29.1, R30.2, R46.2, R47.2, RSENSE1.2, S1.8 (VSS), S1.10 (BS0), S1.11 (BS1), S1.12 (BS2), S1.16 (R/W#), S1.17 (E/RD#), S1.21 (D8), S1.22 (D4), S1.23 (D5), S1.24 (D6), S1.25 (D7), S1.29 (SDA), S1.30 (NC_(GND)), SW1.2, SW2.2, SW3.2, U1.4 (SHDN), U1.6 (AGND), U1.7 (GND), U3.2 (GND), U5.5 (GNDANA), U5.18 (GND), U5.35 (GND), U5.42 (GND), U6.4 (V-), U7.2 (CATHODE), U7.3 (CATHODE), U8.2 (CATHODE), U8.3 (CATHODE), U9.2 (CATHODE), U9.3 (CATHODE), U10.3, U12.3, U14.1 (GND), U15.4 (VSS), U16.7 (GND)
GND_C: C13.2, C19.2, C36.2, P12.1, R28.1, U2.32 (DIR), U2.33 (GND), U2.34 (HVGND), U7.5, U8.5, U9.5, U12.4
GND_C2: C12.2, C18.2, C35.2, R28.2, U4.32 (DIR), U4.33 (GND), U4.34 (HVGND)
JOY: JS1.5 (D_(rigth)), JS2.4 (B_(right)), R18.1, R19.2, U5.10 (EXTINT5EXTWAKE5/AIN5/AIN1/VOUT1/OAPOS2/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)
LE: R37.2, U5.13 (NMI/AIN16/X0Y6/SERCOM0PAD0/SERCOM2PAD0/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)
LE_C: P8.1, R26.2, U2.38 (LE), U4.38 (LE)
unnamed: C1.1, C2.1, L1.1, SW5.1, U1.2 (VCC)
unnamed: C3.1, U1.5 (REF)
unnamed: C7.1, S1.2 (C2P)
unnamed: C7.2, S1.3 (C2N)
unnamed: C8.1, S1.28 (VCC)
unnamed: C9.1, S1.4 (C1P)
unnamed: C9.2, S1.5 (C1N)
unnamed: C10.1, S1.27 (VCOMH)
unnamed: C11.1, R12.1, R13.1
unnamed: C11.2, U3.3 (IN)
unnamed: C16.1, C17.2, R31.2, U6.2 (-)
unnamed: C20.1, U5.43 (VSW)
unnamed: C23.2, U5.1 (XIN32/EXTINT0EXTWAKE0/SERCOM1PAD0/TCC2W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), Y1.1
unnamed: C25.2, U5.2 (XOUT32/EXTINT1EXTWAKE1/SERCOM1PAD1/TCC2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), Y1.2
unnamed: C28.2, D2.2 (A), R10.2, U16.1
unnamed: C29.2, D3.1 (K), R44.2, U16.9
unnamed: C31.2, R11.1, R29.2, U16.3
unnamed: C37.2, R26.1, R39.1, U7.6 (COLLECTOR)
unnamed: D1.2 (A), L1.2, T1.2 (D)
unnamed: D2.1 (K), D3.2 (A), R10.1, R44.1, U16.4
unnamed: FLUXL_1_1.1, U2.44 (HV_OUT_4)
unnamed: FLUXL_1_2.1, FLUXL_1_2b1.1, P4.1, U2.43 (HV_OUT_3)
unnamed: FLUXL_1_3.1, U2.42 (HV_OUT_2)
unnamed: FLUXL_1_4.1, U2.41 (HV_OUT_1)
unnamed: FLUXL_1_5.1, U2.24 (HV_OUT_64)
unnamed: FLUXL_1_6.1, U2.23 (HV_OUT_63)
unnamed: FLUXL_1_7.1, FLUXL_1_7b1.1, U2.22 (HV_OUT_62)
unnamed: FLUXL_1_8.1, U2.21 (HV_OUT_61)
unnamed: FLUXL_2_1.1, U2.47 (HV_OUT_7)
unnamed: FLUXL_2_2.1, U2.48 (HV_OUT_8)
unnamed: FLUXL_2_3.1, U2.46 (HV_OUT_6)
unnamed: FLUXL_2_4.1, U2.45 (HV_OUT_5)
unnamed: FLUXL_2_5.1, U2.20 (HV_OUT_60)
unnamed: FLUXL_2_6.1, U2.19 (HV_OUT_59)
unnamed: FLUXL_2_7.1, U2.17 (HV_OUT_57)
unnamed: FLUXL_2_8.1, U2.18 (HV_OUT_58)
unnamed: FLUXL_3_1.1, U2.51 (HV_OUT_11)
unnamed: FLUXL_3_2.1, U2.50 (HV_OUT_10)
unnamed: FLUXL_3_3.1, U2.52 (HV_OUT_12)
unnamed: FLUXL_3_4.1, U2.49 (HV_OUT_9)
unnamed: FLUXL_3_5.1, U2.16 (HV_OUT_56)
unnamed: FLUXL_3_6.1, U2.13 (HV_OUT_53)
unnamed: FLUXL_3_7.1, U2.15 (HV_OUT_55)
unnamed: FLUXL_3_8.1, U2.14 (HV_OUT_54)
unnamed: FLUXL_4_1.1, U2.54 (HV_OUT_14)
unnamed: FLUXL_4_2.1, U2.55 (HV_OUT_15)
unnamed: FLUXL_4_3.1, U2.56 (HV_OUT_16)
unnamed: FLUXL_4_4.1, U2.53 (HV_OUT_13)
unnamed: FLUXL_4_5.1, U2.12 (HV_OUT_52)
unnamed: FLUXL_4_6.1, U2.9 (HV_OUT_49)
unnamed: FLUXL_4_7.1, U2.10 (HV_OUT_50)
unnamed: FLUXL_4_8.1, U2.11 (HV_OUT_51)
unnamed: FLUXL_5_1.1, U2.58 (HV_OUT_18)
unnamed: FLUXL_5_2.1, U2.59 (HV_OUT_19)
unnamed: FLUXL_5_3.1, U2.60 (HV_OUT_20)
unnamed: FLUXL_5_4.1, U2.57 (HV_OUT_17)
unnamed: FLUXL_5_5.1, U2.8 (HV_OUT_48)
unnamed: FLUXL_5_6.1, U2.5 (HV_OUT_45)
unnamed: FLUXL_5_7.1, U2.6 (HV_OUT_46)
unnamed: FLUXL_5_8.1, U2.7 (HV_OUT_47)
unnamed: FLUXL_6_1.1, U2.61 (HV_OUT_21)
unnamed: FLUXL_6_2.1, U2.62 (HV_OUT_22)
unnamed: FLUXL_6_3.1, U2.63 (HV_OUT_23)
unnamed: FLUXL_6_4.1, U2.64 (HV_OUT_24)
unnamed: FLUXL_6_5.1, U2.1 (HV_OUT_41)
unnamed: FLUXL_6_6.1, U2.2 (HV_OUT_42)
unnamed: FLUXL_6_7.1, U2.3 (HV_OUT_43)
unnamed: FLUXL_6_8.1, U2.4 (HV_OUT_44)
unnamed: FLUXL_7_1.1, U2.65 (HV_OUT_25)
unnamed: FLUXL_7_2.1, U2.69 (HV_OUT_29)
unnamed: FLUXL_7_3.1, U2.68 (HV_OUT_28)
unnamed: FLUXL_7_4.1, U2.72 (HV_OUT_32)
unnamed: FLUXL_7_5.1, U2.73 (HV_OUT_33)
unnamed: FLUXL_7_6.1, U2.78 (HV_OUT_38)
unnamed: FLUXL_7_7.1, U2.76 (HV_OUT_36)
unnamed: FLUXL_7_8.1, U2.80 (HV_OUT_40)
unnamed: FLUXL_8_1.1, U2.70 (HV_OUT_30)
unnamed: FLUXL_8_2.1, U2.66 (HV_OUT_26)
unnamed: FLUXL_8_3.1, U2.67 (HV_OUT_27)
unnamed: FLUXL_8_4.1, U2.71 (HV_OUT_31)
unnamed: FLUXL_8_5.1, U2.74 (HV_OUT_34)
unnamed: FLUXL_8_6.1, U2.77 (HV_OUT_37)
unnamed: FLUXL_8_7.1, U2.79 (HV_OUT_39)
unnamed: FLUXL_8_8.1, U2.75 (HV_OUT_35)
unnamed: FLUXL_9_1.1, U4.75 (HV_OUT_35)
unnamed: FLUXL_9_2.1, U4.79 (HV_OUT_39)
unnamed: FLUXL_9_3.1, U4.77 (HV_OUT_37)
unnamed: FLUXL_9_4.1, U4.74 (HV_OUT_34)
unnamed: FLUXL_9_5.1, U4.71 (HV_OUT_31)
unnamed: FLUXL_9_6.1, U4.67 (HV_OUT_27)
unnamed: FLUXL_9_7.1, U4.66 (HV_OUT_26)
unnamed: FLUXL_9_8.1, U4.70 (HV_OUT_30)
unnamed: FLUXL_10_1.1, U4.80 (HV_OUT_40)
unnamed: FLUXL_10_2.1, U4.76 (HV_OUT_36)
unnamed: FLUXL_10_3.1, U4.78 (HV_OUT_38)
unnamed: FLUXL_10_4.1, U4.73 (HV_OUT_33)
unnamed: FLUXL_10_5.1, U4.72 (HV_OUT_32)
unnamed: FLUXL_10_6.1, U4.68 (HV_OUT_28)
unnamed: FLUXL_10_7.1, U4.69 (HV_OUT_29)
unnamed: FLUXL_10_8.1, U4.65 (HV_OUT_25)
unnamed: FLUXL_11_1.1, U4.4 (HV_OUT_44)
unnamed: FLUXL_11_2.1, U4.3 (HV_OUT_43)
unnamed: FLUXL_11_3.1, U4.2 (HV_OUT_42)
unnamed: FLUXL_11_4.1, U4.1 (HV_OUT_41)
unnamed: FLUXL_11_5.1, U4.64 (HV_OUT_24)
unnamed: FLUXL_11_6.1, U4.63 (HV_OUT_23)
unnamed: FLUXL_11_7.1, U4.62 (HV_OUT_22)
unnamed: FLUXL_11_8.1, U4.61 (HV_OUT_21)
unnamed: FLUXL_12_1.1, U4.7 (HV_OUT_47)
unnamed: FLUXL_12_2.1, U4.6 (HV_OUT_46)
unnamed: FLUXL_12_3.1, U4.5 (HV_OUT_45)
unnamed: FLUXL_12_4.1, U4.8 (HV_OUT_48)
unnamed: FLUXL_12_5.1, U4.57 (HV_OUT_17)
unnamed: FLUXL_12_6.1, U4.60 (HV_OUT_20)
unnamed: FLUXL_12_7.1, U4.59 (HV_OUT_19)
unnamed: FLUXL_12_8.1, U4.58 (HV_OUT_18)
unnamed: FLUXL_13_1.1, U4.11 (HV_OUT_51)
unnamed: FLUXL_13_2.1, U4.10 (HV_OUT_50)
unnamed: FLUXL_13_3.1, U4.9 (HV_OUT_49)
unnamed: FLUXL_13_4.1, U4.12 (HV_OUT_52)
unnamed: FLUXL_13_5.1, U4.53 (HV_OUT_13)
unnamed: FLUXL_13_6.1, U4.56 (HV_OUT_16)
unnamed: FLUXL_13_7.1, U4.55 (HV_OUT_15)
unnamed: FLUXL_13_8.1, U4.54 (HV_OUT_14)
unnamed: FLUXL_14_1.1, U4.14 (HV_OUT_54)
unnamed: FLUXL_14_2.1, U4.15 (HV_OUT_55)
unnamed: FLUXL_14_3.1, U4.13 (HV_OUT_53)
unnamed: FLUXL_14_4.1, U4.16 (HV_OUT_56)
unnamed: FLUXL_14_5.1, U4.49 (HV_OUT_9)
unnamed: FLUXL_14_6.1, U4.52 (HV_OUT_12)
unnamed: FLUXL_14_7.1, U4.50 (HV_OUT_10)
unnamed: FLUXL_14_8.1, U4.51 (HV_OUT_11)
unnamed: FLUXL_15_1.1, U4.18 (HV_OUT_58)
unnamed: FLUXL_15_2.1, U4.17 (HV_OUT_57)
unnamed: FLUXL_15_3.1, U4.19 (HV_OUT_59)
unnamed: FLUXL_15_4.1, U4.20 (HV_OUT_60)
unnamed: FLUXL_15_5.1, U4.45 (HV_OUT_5)
unnamed: FLUXL_15_6.1, U4.46 (HV_OUT_6)
unnamed: FLUXL_15_7.1, U4.48 (HV_OUT_8)
unnamed: FLUXL_15_8.1, U4.47 (HV_OUT_7)
unnamed: FLUXL_16_1.1, U4.21 (HV_OUT_61)
unnamed: FLUXL_16_2.1, FLUXL_16_2b1.1, U4.22 (HV_OUT_62)
unnamed: FLUXL_16_3.1, U4.23 (HV_OUT_63)
unnamed: FLUXL_16_4.1, U4.24 (HV_OUT_64)
unnamed: FLUXL_16_5.1, U4.41 (HV_OUT_1)
unnamed: FLUXL_16_6.1, U4.42 (HV_OUT_2)
unnamed: FLUXL_16_7.1, FLUXL_16_7b1.1, U4.43 (HV_OUT_3)
unnamed: FLUXL_16_8.1, U4.44 (HV_OUT_4)
unnamed: J1.A5 (CC1), R47.1
unnamed: J1.B5 (CC2), R46.1
unnamed: JS1.1 (A_(up)), JS2.1 (A_(up)), R21.1
unnamed: JS1.2 (B_(left)), JS2.3 (C_(left)), R20.1, R21.2
unnamed: JS1.3 (C_(down)), JS2.6 (D_(down)), R19.1, R20.2
unnamed: LED1.2 (A), R6.2
unnamed: LED2.2 (A), R4.2
unnamed: LED3.2 (A), R8.2
unnamed: R1.1, R9.2, U15.7 (PB0)
unnamed: R2.2, U1.3 (FB), U15.5 (PA0), U15.6 (PW0)
unnamed: R3.1, S1.26 (REF)
unnamed: R22.2, R30.1, U6.5 (+)
unnamed: R24.1, R35.1, U9.7 (COLLECTOR)
unnamed: R25.1, R42.1, U8.6 (COLLECTOR)
unnamed: R32.1, U7.1 (ANODE)
unnamed: R34.1, U9.1 (ANODE)
unnamed: R36.1, U8.1 (ANODE)
unnamed: R37.1, U7.4 (ANODE)
unnamed: R40.1, U8.4 (ANODE)
unnamed: R41.1, U9.4 (ANODE)
unnamed: R43.1, U9.6 (COLLECTOR)
unnamed: R45.1, U10.1
unnamed: R48.1, U11.1
unnamed: R49.1, U12.1
unnamed: R51.1, U13.1
unnamed: RSENSE1.1, T1.3 (S), U1.8 (CS)
unnamed: SP1.1, U3.1 (OUT-)
unnamed: SP1.2, U3.6 (OUT+)
unnamed: T1.1 (G), U1.1 (EXT)
unnamed: U2.26 (DIO_A), U4.39 (DIO_B)
unnamed: U6.3 (+), U6.6 (-), U6.7
unnamed: U10.2, U16.2
unnamed: U11.2, U16.6
unnamed: U12.2, U16.12
unnamed: U13.2, U16.10
unnamed: U16.5, U16.8, U16.11, U16.13
POL: R36.2, U5.23 (XIN/EXTINT14/SERCOM2PAD2/SERCOM4PAD2/TC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)
POL_C: R14.1, R38.1, U4.30 (POL), U8.7 (COLLECTOR)
POL_C2: R14.2, U2.30 (POL)
RESET: J2.10, R5.1, SW3.1, U5.40 (~RESET~)
RX_LED: R6.1, U5.48 (EXTINT3/AIN11/SERCOM5PAD1/TC2WO1/SUPCVB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)
SENS_PAD: P16.1, U5.47 (EXTINT2/AIN10/SERCOM5PAD0/TC2WO0/SUPCOU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)
SPK: R12.2, U5.3 (EXTINT2EXTWAKE2/AIN0/Y0/VOUT0/OANEG0/PA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)
SW1: SW1.1, U5.11 (EXTINT6EXTWAKE6/AIN6/AIN2/Y4/OAPOS0/SER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)
SW2: SW2.1, U5.29 (EXTINT4/X8/SERCOM5PAD2/SERCOM3PAD2/TC3W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)
SW3: JS1.6 (Center), JS2.2 (Center), U5.30 (EXTINT5/X9/SERCOM5PAD3/SERCOM3PAD3/TC3W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)
SWCLK: J2.4, U5.45 (EXTINT10/SERCOM1PAD2/TCC1WO0/CORTEXM0PS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)
SWDIO: J2.2, U5.46 (EXTINT11/SERCOM1PAD3/TCC1WO1/SWDIO/CCL1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)
VDD_C: C13.1, C19.1, C36.1, C37.1, P3.1, R27.2, R33.2, R35.2, R38.2, R39.2, R42.2, R43.2, U2.31 (VDD), U7.8 (VCC), U8.8 (VCC), U9.8 (VCC), U13.3
VDD_C2: C12.1, R27.1, U4.31 (VDD)
VSENS: R9.1, U5.9 (EXTINT4EXTWAKE4/VREFB/AIN4/AIN0/OAOUT2/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)
V_CS: U5.22 (ACCMP1/TC2WO1/SERCOM4P1/SERCOM2P1/PA13), U15.1 (~CS)
V_GND: C16.2, P1.1, P14.1
V_HV: C4.1, C6.1, D1.1 (K), R2.1, U11.4
V_HV_C: C18.1, C35.1, P7.1, U2.25 (VPP), U4.40 (VPP), U10.4, U11.3
V_SCK: U5.28 (EXTINT3/X7/SERCOM1PAD3/SERCOM3PAD3/TC4W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), U15.2 (SCK)
V_SI: U5.25 (EXTINT0/X4/SERCOM1PAD0/SERCOM3PAD4/TCC2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), U15.3 (SI)
V_USB: C5.1, C27.2, C32.1, J1.A4 (VBUS), J1.A9 (VBUS), J1.B4 (VBUS), J1.B9 (VBUS), R45.2, R48.2, R49.2, R51.2, SW5.2, U13.4, U14.3 (VI), U16.14 (VCC)

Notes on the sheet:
65-260VDC
Display
AC SWITCHER
HIGH VOLTAGE BOOST CONVERTER
FEEDBACK AMPLIFIER
INTERFACE
HIGH VOLTAGE DRIVER
OPTO ISOLATORS
MICROCONTROLLER
OLED DISPLAY
D6 / changed
A0 / vout
changed
10k
D3 / changed
LED? MKR
A3 / A3? MKR
A4? MKR
D8 / A5? MKR
D9 / A6? MKR
D4 / SDA? MKR
SCL? MKR
D1 / PWM2? MKR
D0 / PWM3? MKR
D23 / PWM4? MKR
D24 / PWM5? MKR
22/ MOSI? MKR
? / SCK? MKR
D2 / DATA? MKR
MISO? MKR
MOSI? MKR / SERCOM 1
SCK? MKR / SERCOM1
D10 / USB_PAD4??? MKR / SERCOM1
MISO? MKR / SERCOM1
PAD6? MKR
D7 / PAD7? MKR
PAD7? MKR
PAD0? MKR
TX? MKR
RX? MKR



Board: 2 copper layers, 124.0 x 112.0 mm, 269 parts (121 on the bottom side), 232 nets.

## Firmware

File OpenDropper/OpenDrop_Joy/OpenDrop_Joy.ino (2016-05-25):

/*
  Blink
  Turns on an LED on for one second, then off for one second, repeatedly.

  Most Arduinos have an on-board LED you can control. On the Uno and
  Leonardo, it is attached to digital pin 13. If you're unsure what
  pin the on-board LED is connected to on your Arduino model, check
  the documentation at http://arduino.cc

  This example code is in the public domain.

  modified 8 May 2014
  by Scott Fitzgerald
 */

#include <SPI.h>
#include <Wire.h>
#include <Adafruit_GFX.h>
#include <Adafruit_SSD1306.h>

#include <OpenDrop.h>
#include "hardware_def.h"


// If using software SPI (the default case):
#define OLED_MOSI   2
#define OLED_CLK   3
#define OLED_DC    11
#define OLED_CS    12
#define OLED_RESET 13
Adafruit_SSD1306 display(OLED_MOSI, OLED_CLK, OLED_DC, OLED_RESET, OLED_CS);

#define BL_pin         9           // BL Pin
#define LE_pin          4           // LE Pin
#define CLK_pin         15           // CLK Pin
#define DI_pin         16           // Digital Out Pin

#define SW1_pin         8           // Buton 1 pin
#define SW2_pin         A5           // Buton 1 pin
#define SW3_pin         7           // Buton 1 pin
#define JOY_pin         A4           // Buton 1 pin

#define ESP_RESET_pin   A3           // Buton 1 pin
#define ESP_GPIO0_pin   10           // Buton 1 pin
#define ESP_RX_pin      1           // Buton 1 pin
#define ESP_TX_pin      0           // Buton 1 pin


#define LED_LIGHT_pin         5           // Digital  Pin for LEDs
#define SPK_pin       6           // Digital Pin for speaker

boolean sound_flag=true;           // Digital Out Pin 2
boolean light_flag=true;           // Digital Out Pin 2
int JOY_value;

  Drop drop[] = {Drop(1),Drop(1),Drop(1)};
  bool Fluxls[FluxlPad_width][FluxlPad_heigth];
  
  
// the setup function runs once when you press reset or power the board
void setup() {
  // initialize digital pin 13 as an output.


  pinMode(BL_pin, OUTPUT); //BL pin
  digitalWrite(BL_pin, HIGH);   // set BL 
  pinMode(LE_pin, OUTPUT); //LE pin
  digitalWrite(LE_pin, LOW);   // set LE 
  pinMode(CLK_pin, OUTPUT); //SCK pin
  digitalWrite(CLK_pin, LOW);   // set SCK 
  pinMode(DI_pin, OUTPUT); //LE pin
  digitalWrite(DI_pin, LOW);   // set LE 

  pinMode(LED_LIGHT_pin, OUTPUT); //SCK pin
  
  pinMode(SW1_pin, INPUT); 
  digitalWrite(SW1_pin, HIGH);  
  pinMode(SW2_pin, INPUT); 
  digitalWrite(SW2_pin, HIGH);  
  pinMode(SW3_pin, INPUT); 
  digitalWrite(SW3_pin, HIGH);  
  pinMode(JOY_pin, INPUT); 

  Serial.begin(9600);

  // by default, we'll generate the high voltage from the 3.3v line internally! (neat!)
  display.begin(SSD1306_SWITCHCAPVCC);
  // init done
  
  // Show image buffer on the display hardware.
  // Since the buffer is intialized with an Adafruit splashscreen
  // internally, this will display the splashscreen.
  display.display();
  delay(2000);

  // Clear the buffer.
  display.clearDisplay();

display.setTextSize(1);
  display.setTextColor(WHITE);
  display.setCursor(5,20);
  display.println("Loading protocol...");
  display.display();
  delay(500);
  display.setCursor(5,29);
  display.println("Press Start");
display.display();


  drop[0].begin(6,3);
  drop[1].begin(1,1);
  drop[2].begin(1,1);
  
    update();

  
  tone(SPK_pin,2000,100);
  delay(100);
  tone(SPK_pin,2000,100);
  delay(200);
  while(digitalRead(SW2_pin) == HIGH);



if (light_flag)   digitalWrite(LED_LIGHT_pin, HIGH);   // set SCK 
}


// the loop function runs over and over again forever
void loop() {
  
int del_time=100;

JOY_value = analogRead(JOY_pin);

  while(JOY_value>950)
   JOY_value = analogRead(JOY_pin);


  Serial.print(JOY_value);


if  (JOY_value<300)
  drop[0].move_right();

if  ((JOY_value>700)&&(JOY_value<950))
  drop[0].move_up();
  
if  ((JOY_value>600)&&(JOY_value<700))
  drop[0].move_left();
  
if  ((JOY_value>450)&&(JOY_value<600))
  drop[0].move_down();

  update();
  delay(del_time);
  JOY_value = analogRead(JOY_pin);

}



void update()
{
  
const byte pad_lookup_x [64] PROGMEM = {
0,0,0,0,1,1,1,1,
2,2,2,2,3,3,3,3,
4,4,4,4,5,5,5,5,
6,7,7,6,6,7,7,6,
6,7,7,6,7,6,7,6,
5,5,5,5,4,4,4,4,
3,3,3,3,2,2,2,2,
1,1,1,1,0,0,0,0
};

const byte pad_lookup_y [64] PROGMEM = {
3,2,1,0,3,2,0,1,
3,1,0,2,3,0,1,2,
3,0,1,2,0,1,2,3,
0,1,2,2,1,0,3,3,
4,4,7,6,5,5,6,7,
4,5,6,7,5,6,7,4,
5,6,7,4,5,7,6,4,
6,7,5,4,7,6,5,4
};




clear_Fluxels();                     //clear Fluxel Array


//Fill Fluxel Array
for (int i = 0; i <3 ; i++) 
{
  Fluxls[drop[i].position_x()][drop[i].position_y()]=true;
};


// clear Display
  display.clearDisplay();

// draw Grid
  for (int x = 1; x <FluxlPad_width ; x++) 
    for (int y = 1; y <FluxlPad_heigth ; y++) 
  display.drawPixel(x*7+4,y*7+4,WHITE);
  
  
// draw Fluxels
      for (int x = 0; x <FluxlPad_width ; x++) 
    for (int y = 0; y <FluxlPad_heigth ; y++) 
   if (Fluxls[x][y]) {
           display.fillRect(x*7+5, y*7+5, 6,6, 1);
    }
     
// draw Rect
     display.drawRect(4, 4, 114,58, 1);

// update display
    display.display();
   
   

// Fill chip

    digitalWrite(LE_pin, LOW);   // set LE 
    digitalWrite(CLK_pin, LOW);   // set SCK 
   
    for (int i = 0; i <64 ; i++) 

{
   digitalWrite(DI_pin,Fluxls[pad_lookup_x[i]][pad_lookup_y[i]]);

   digitalWrite(CLK_pin, HIGH);   // set LE
   digitalWrite(CLK_pin, LOW);   // set LE
 
  //Serial.println(Fluxls[pad_lookup_x[i]][pad_lookup_y[i]]);
   };
   
     for (int i = 0; i <64 ; i++) 
{
   digitalWrite(DI_pin,Fluxls[15-pad_lookup_x[i]][7-pad_lookup_y[i]]);

   digitalWrite(CLK_pin, HIGH);   // set LE
   digitalWrite(CLK_pin, LOW);   // set LE
 
  //Serial.println(Fluxls[pad_lookup_x[i]][pad_lookup_y[i]]);
   };
   
   
  
    digitalWrite(LE_pin, HIGH);   // set LE 
    digitalWrite(LE_pin, LOW);   // set LE 
    
 if(sound_flag)   tone(SPK_pin,2400,50);  
  
};


void clear_Fluxels()
{
    for (int x = 0; x <FluxlPad_width ; x++) 
    for (int y = 0; y <FluxlPad_heigth ; y++) 
  Fluxls[x][y]=false;

};

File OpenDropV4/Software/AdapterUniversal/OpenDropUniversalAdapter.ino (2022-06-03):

/*******************************************************************************************************
  Programs for Arduino - Copyright of the author Stuart Robinson - 09/02/20

  This program is supplied as is, it is up to the user of the program to decide if the program is
  suitable for the intended purpose and free from errors.
*******************************************************************************************************/

/*******************************************************************************************************
  Program Operation - Configures a Arduino M0 Pro to act as an I2C slave and prints the received I2C
  payload\buffer to the Serial Monitor. Uses the standard M0 Pro I2C port.

  Designed to be used with test program '60_I2C_Transmit_to_Slave_Test' which transmits a 6 byte payload,
  the first byte is the address being sent to, then ASCII characters '0' to '4'. Sample printout below.

  12 Process buffer > 18 30 31 32 33 34
  13 Process buffer > 18 30 31 32 33 34
  
  Note that if this slave program is running and an I2C scanner is run on the board there will be a device
  detected on the Slave_Address used and 0x28 which is the Arduino Zero's EDBG which is connected as a 
  slave to the processor.

  Serial monitor baud rate is set at 9600.

*******************************************************************************************************/

#include <Wire.h>
#include <Arduino.h>

#define LED1 13                           //on board LED on M0 PRo
#define Slave_Address 0x18                //slave address for this board

#define ADAPTER_IODIR 0x00
#define ADAPTER_GPIO 0x01
#define ADAPTER_GETTEMP_H_1 0x02
#define ADAPTER_GETTEMP_L_1 0x03
#define ADAPTER_GETTEMP_H_2 0x04
#define ADAPTER_GETTEMP_L_2 0x05
#define ADAPTER_GETTEMP_H_3 0x06
#define ADAPTER_GETTEMP_L_3 0x07
#define ADAPTER_SETTEMP_H_1 0x08
#define ADAPTER_SETTEMP_L_1 0x09
#define ADAPTER_SETTEMP_H_2 0x0A
#define ADAPTER_SETTEMP_L_2 0x0B
#define ADAPTER_SETTEMP_H_3 0x0C
#define ADAPTER_SETTEMP_L_3 0x0D



#define STBY_regpos         6
#define MODE_regpos         4
#define BOOST_regpos        5
#define PHASE_A_regpos      1
#define ENABLE_A_regpos     0
#define PHASE_B_regpos      3
#define ENABLE_B_regpos     2

#define stby_Pin      10
#define mode_Pin      12
#define boostPin      5
#define phaseA_Pin    7
#define enableA_Pin   8
#define phaseB_Pin    11
#define enableB_Pin   6

#define PIDp 0.015
#define PIDi 0.000035//0.0001
#define PIDd 0.0007

uint16_t I2CmessagesCount;
uint8_t I2Cbuffer[64];                    //buffer for received I2C payload
boolean I2CbufferReady = false;
uint8_t I2CbytesReceived;
uint8_t ReceivedAddr=0;
uint8_t ReceivedData=0;


float TEMPset1;
float TEMPdif1;
float TEMPi1;
bool PIDIntegration1 = true;
float TEMPcontrol1;
float TEMPdif_a1[10];
float TEMPd1;

float TEMPset2;
float TEMPdif2;
float TEMPi2;
bool PIDIntegration2 = true;
float TEMPcontrol2;
float TEMPdif_a2[10];
float TEMPd2;

float TEMPset3;
float TEMPdif3;
float TEMPi3;
bool PIDIntegration3 = true;
float TEMPcontrol3;
float TEMPdif_a3[10];
float TEMPd3;


long TEMPclick=0;

int IODIR_byte;
int GPIO_byte;

const int TemperatureSensor1 = A1;  // Analog input pin that the temperature sensor is attached to
const int TemperatureSensor2 = A2;  // Analog input pin that the temperature sensor is attached to
const int TemperatureSensor3 = A3;  // Analog input pin that the temperature sensor is attached to

const int heaterPin1 = 9;
const int heaterPin2 = 4;
const int heaterPin3 = 3;



int pp;

int outputValue = 0;        // value output to the PWM (heater)

float temperature_mean1 =0;
float temperature_mean2 =0;
float temperature_mean3 =0;
float temperature1 = 0;
float temperature2 = 0;
float temperature3 = 0;

float getTemperature(int analogInPin)

{
const int NTC_B = 3435;
const float NTC_TN = 298.15;
const int NTC_RN = 10000;
const float NTC_R0 = 4.7;

int sensorValue;
float sensorVoltage;
float sensorResistance;
float temperature;


  sensorValue = analogRead(analogInPin);
  sensorVoltage=3.3*sensorValue/4096;
  sensorResistance=((sensorVoltage*NTC_R0)/(3.3-sensorVoltage));
  temperature=  1/(log(sensorResistance*1000/NTC_RN)/NTC_B+1/NTC_TN)-273.15 ;
  
return temperature;
};

void setHeater(float temperature,float power,int heaterPin)
{
const int t0=25;
const int tmax=130;
int pinPower;


  if (temperature>tmax) temperature=tmax;
  if (temperature<t0) temperature=t0;
  
if (power>0){
  pinPower=constrain(255*(power/(1-(temperature-t0)/(tmax-t0))), 0, 255);
   analogWrite(heaterPin,pinPower);
   pp=pinPower;
  } else
  { 
     pinPower=constrain(255*(1+power)*((temperature-t0-20)/(tmax-t0)), 0, 255);
    // pinPower=0;
      analogWrite(heaterPin,pinPower);
      pp=pinPower;
    }

  };

void runPID()
{
   TEMPcontrol1= PIDp*TEMPdif1+PIDd*TEMPd1+(int)PIDIntegration1*PIDi*TEMPi1;
  setHeater(temperature_mean1, TEMPcontrol1,heaterPin1);

   TEMPcontrol2= PIDp*TEMPdif2+PIDd*TEMPd2+(int)PIDIntegration2*PIDi*TEMPi2;
  setHeater(temperature_mean2, TEMPcontrol2,heaterPin2);

   TEMPcontrol3= PIDp*TEMPdif3+PIDd*TEMPd3+(int)PIDIntegration3*PIDi*TEMPi3;
  setHeater(temperature_mean3, TEMPcontrol3,heaterPin3);
  };


void setup()
{
  

  pinMode(heaterPin1, OUTPUT);
  pinMode(heaterPin2, OUTPUT);
  pinMode(heaterPin3, OUTPUT);

  digitalWrite(heaterPin1, LOW);
  digitalWrite(heaterPin2, LOW);
  digitalWrite(heaterPin3, LOW);


      

  Wire.begin(Slave_Address);
  Wire.onReceive(receiveEvent);        //data from slave recieved
  Wire.onRequest(requestEvent);        //data from slave recieved

  configureAdc();
  analogReadResolution(12);
  pinMode(17, OUTPUT);


}

void loop()
{

  TEMPdif1=TEMPset1-temperature_mean1;
 // if (abs(TEMPdif)<10) PIDIntegration=true; else {PIDIntegration=false;TEMPi=0;};
  TEMPi1=TEMPi1+(TEMPset1-temperature_mean1);
  if (TEMPi1>8000)TEMPi1=8000;
   if (TEMPi1<-8000)TEMPi1=-8000;

  TEMPdif2=TEMPset2-temperature_mean2;
 // if (abs(TEMPdif)<10) PIDIntegration=true; else {PIDIntegration=false;TEMPi=0;};
  TEMPi2=TEMPi2+(TEMPset2-temperature_mean2);
  if (TEMPi2>8000)TEMPi2=8000;
   if (TEMPi2<-8000)TEMPi2=-8000;

   TEMPdif3=TEMPset3-temperature_mean3;
 // if (abs(TEMPdif)<10) PIDIntegration=true; else {PIDIntegration=false;TEMPi=0;};
  TEMPi3=TEMPi3+(TEMPset3-temperature_mean3);
  if (TEMPi3>8000)TEMPi3=8000;
   if (TEMPi3<-8000)TEMPi3=-8000;
   
  runPID();
  
  if (millis()-TEMPclick>200) {
  TEMPclick=millis();
  TEMPd1=TEMPdif_a1[4]-TEMPset1-temperature1;
  TEMPdif_a1[4]=TEMPdif_a1[3];
  TEMPdif_a1[3]=TEMPdif_a1[2];
  TEMPdif_a1[2]=TEMPdif_a1[1];
  TEMPdif_a1[1]=TEMPdif_a1[0];
  TEMPdif_a1[0]=TEMPdif1;
 
  TEMPd2=TEMPdif_a2[4]-TEMPset2-temperature2;
  TEMPdif_a2[4]=TEMPdif_a2[3];
  TEMPdif_a2[3]=TEMPdif_a2[2];
  TEMPdif_a2[2]=TEMPdif_a2[1];
  TEMPdif_a2[1]=TEMPdif_a2[0];
  TEMPdif_a2[0]=TEMPdif2;
 
  TEMPd3=TEMPdif_a3[4]-TEMPset3-temperature3;
  TEMPdif_a3[4]=TEMPdif_a3[3];
  TEMPdif_a3[3]=TEMPdif_a3[2];
  TEMPdif_a3[2]=TEMPdif_a3[1];
  TEMPdif_a3[1]=TEMPdif_a3[0];
  TEMPdif_a3[0]=TEMPdif3;
  
  }

 temperature1=getTemperature(TemperatureSensor1);
 temperature_mean1= (temperature_mean1*39+temperature1)/40;
 temperature2=getTemperature(TemperatureSensor2);
 temperature_mean2= (temperature_mean2*39+temperature2)/40;
 temperature3=getTemperature(TemperatureSensor3);
 temperature_mean3= (temperature_mean3*39+temperature3)/40;

 delay(5);
}





void receiveEvent(int howMany)
{
  uint8_t index;
  uint8_t receiveptr = 0;

  I2CbufferReady = false;               //buffer not saved yet  
  I2CbytesReceived = howMany;           //save the numebr of bytes available
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

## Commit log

2016-02-15 OpenDrop V2
    Complete design files of OpenDrop V2 Proto
    [OpenDropV2-B.Paste.gbr, OpenDropV2-F.Paste.gbr, OpenDropV2.GBL, OpenDropV2.GBO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]
2016-03-07 changed library paths to be relative and point to GaudiLabsPartsLibrary and arduino_micro_shield within the repository
2016-04-28 started with corrections for V2.1
    work in progress
    [OpenDropV2.kicad_pcb, OpenDropV2.sch]
2016-05-03 More modifications and corrections for Version 2.1
    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
    [OpenDropV2.kicad_pcb, OpenDropV2.sch]
2016-05-09 added interfacing for esp-01 module, moved sda/scl, removed p3, moved BL
    [OpenDropV2.sch]
2016-05-09 changed pin numbering on esp-01 module symbol
2016-05-09 first try at making open drop with esp201 only and no micro
    [OpenDropV2-ESP201.kicad_pcb, OpenDropV2-ESP201.sch]
2016-05-09 put fet at ground for led lights
    [OpenDropV2-ESP201.sch]
2016-05-11 Production Version of V2.1
    Hopefully...
    [OpenDropV2-B.Cu.gbr, OpenDropV2-B.Mask.gbr, OpenDropV2-B.Paste.gbr, OpenDropV2-B.SilkS.gbr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]
2016-05-12 Production Version 2.1 with Gerber Files
    Version Bittie
    [OpenDropV2-B.Cu.gbr, OpenDropV2-B.Mask.gbr, OpenDropV2-B.Paste.gbr, OpenDropV2-B.SilkS.gbr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]
2016-05-24 cleaned up folder structure
    V2-ESP01 and C2-ESP201
    [OpenDropV2-B.Cu.gbr, OpenDropV2-B.Mask.gbr, OpenDropV2-B.Paste.gbr, OpenDropV2-B.SilkS.gbr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]
2016-06-02 Added Carrier and BOM21
    [Cardridge_PCB.dxf, OpenDropV21BOM.ods, PCBFrame-B.Cu.gbr, PCBFrame-B.Mask.gbr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]
2016-09-26 Updated Arduino Code to V2.1
    [OpenDropV2-B.Cu.gbr, OpenDropV2-B.Mask.gbr, OpenDropV2-B.Paste.gbr, OpenDropV2-B.SilkS.gbr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]
2017-04-07 Added new OpenDrop Library beta version
    [_saved_OpenDropV2.sch]
2017-12-06 First release OpenDrop V3 yuhuu
    [OpenDropV2-B.Cu.gbr, OpenDropV2-B.Mask.gbr, OpenDropV2-B.Paste.gbr, OpenDropV2-B.SilkS.gbr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]
2018-04-10 Improved design and corrected some errors. Allmost there
    [OpenDropV3-B.Cu.gbr, OpenDropV3-B.Mask.gbr, OpenDropV3-B.Paste.gbr, OpenDropV3-B.SilkS.gbr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]
2018-04-24 Updated OpenDrop V3 to V3.1 and waiting for the PCBs
    [OpenDropV3-B.Cu.gbr, OpenDropV3-B.Mask.gbr, OpenDropV3-B.Paste.gbr, OpenDropV3-B.SilkS.gbr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]
2018-06-12 Added OpenDropper V3 Arduino (Adafruit Feather M0) code to run OpenDrop V3
2018-06-15 Added OpenDrop App First commit
    [OpenDropV31BOM.ods]
2018-07-26 Version 3.2 allmost done
    [OpenDropV3.kicad_pcb, OpenDropV3.sch, OpenDropV31BOM.ods, ProtectiveSticker.dxf]
2018-08-06 Updated to V3_2 Rearranged Folder
    [Cardridge_PCB.dxf, OpenDropV3-B.Cu.gbr, OpenDropV3-B.Mask.gbr, OpenDropV3-B.Paste.gbr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]
2018-08-06 Removed old Gerber Folder Not sure this is the way to do it...
    [OpenDropV3-B.Cu.gbr, OpenDropV3-B.Mask.gbr, OpenDropV3-B.Paste.gbr, OpenDropV3-B.SilkS.gbr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]
2018-08-07 Updated to V32 new marked with (new)
    [OpenDropV3.sch, OpenDropV31BOM.ods, OpenDropV32BOM.ods]
2018-09-14 Production Files V3_2 This is it.
    [OpenDropV3-B.Cu.gbr, OpenDropV3-B.Mask.gbr, OpenDropV3-B.Paste.gbr, OpenDropV3-B.SilkS.gbr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]
2019-06-07 Updated Version of the OpenDrop Controller App Window can scale now.
    [Cardridge_PCB.dxf, OpenDropV2-B.Cu.gbr, OpenDropV2-B.Mask.gbr, OpenDropV2-B.Paste.gbr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]
2020-04-07 Added Version 4 Modular OpenDrop
    [DIMMCartridge-2019-04-09-15-04-31.sch, DIMMCartridge-B.Cu.gbr, DIMMCartridge-B.Mask.gbr, DIMMCartridge-B.Paste.gbr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]
2020-04-29 Ready for second prototype round its not a synth
    [DIMMCartridge-B.Cu.gbr, DIMMCartridge-B.Mask.gbr, DIMMCartridge-B.Paste.gbr, DIMMCartridge-B.SilkS.gbr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]
2020-07-01 Production Version OpenDrop V4 All PCBs, BOMs, Materials and Software
    [Cardridge_PCB.dxf, CartridgBar.STL, DIMMCartridge-2019-04-09-15-04-31.sch, DIMMCartridge-B.Cu.gbr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]
2021-03-31 First design of Magnet Adapter Let's test it.
    [ModulAdapter-2019-04-11-17-09-46.sch, ModulAdapterMagnet-B_Cu.gbr, ModulAdapterMagnet-B_Mask.gbr, ModulAdapterMagnet-B_Paste.gbr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]
2021-08-02 Updated to V4.1 in Software and Electronics
    [NoFrameSent.kicad_pcb, OpenDropV3-B.Cu.gbr, OpenDropV3-B.Mask.gbr, OpenDropV3-B.Paste.gbr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]
2022-06-03 Added Feedback Reading and many updates to hard and software
    [BOMModulAdapter_universal.ods, CartridgBarMagnetV2.STL, CartridgBarUniversal.STL, DIMMCartridge-2019-04-09-15-04-31.sch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]
2023-11-20 Update and new catridge with heated pads
    [BOMModulAdapter_universal.ods, CartridgBarMagnetV2.STL, CartridgBarUniversal.STL, DIMMCartridge-2019-04-09-15-04-31.sch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]
2024-10-21 Updated Module Adapter Basic with protection resistors
    [BOMModulAdapter_basic.ods, ModulAdapter-2019-04-11-17-09-46.sch, ModulAdapter-B.Cu.gbr, ModulAdapter-B.Mask.gbr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]
2024-10-21 Adapter Basic
    [BOMModulAdapter_basic.ods, ModulAdapterBasic-B_Cu.gbr, ModulAdapterBasic-B_Mask.gbr, ModulAdapterBasic-B_Paste.gbr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]
